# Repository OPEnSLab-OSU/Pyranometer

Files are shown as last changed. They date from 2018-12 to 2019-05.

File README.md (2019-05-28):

# Senior-Project-Group3-Pyranometer
Senior Project featuring the OPEnS Pyranometer radiation sensor.

# What is a pyranometer?
Pyranometers are a tool used to measure solar radiation. A typical pyranometer will gather data on the UV, IR, visible spectrum, and full spectrum solar radiation hitting the surface of the earth at a particular spot. This information could be used to help solar panel research, agricultural research, or climate change research. 

The aim of this project was to make an open-source and low-cost. To do this, this pyranometer takes more time to set up. With low-cost electronics and a 3D printer, this pyranometer can be recreated. Currently, it needs two pieces of hardware - a node and a hub. The node sends the measured data to the hub (up to 5km without building interference) where the hub uploads the data to a Google spreadsheet in live time.

# How to set up
The [Setup_Instructions_For_Grading file](https://github.com/OPEnSLab-OSU/Pyranometer/edit/master/README.md/Setup_Instructions_For_Grading.md) contains step by step instructions on what to gather and how to upload the code for this project. The [Assembly_Instructions file](https://github.com/OPEnSLab-OSU/Pyranometer/edit/master/Assembly_Instructions.md) has more in depth information on necessary materials and 3D printing instructions. In that file, the cost of each material is displayed as well as containing some basic flashing instructions.

# Description of other files and folders on this repo
The [LOOM folder](https://github.com/OPEnSLab-OSU/Pyranometer/edit/master/LOOM) holds the code (using OPEnS lab LOOM 1 architecture) for the pyranometer. The node measures and reports data, while the hub is a receiver for loom and uploads data via PushingBox. The [CAD folder](https://github.com/OPEnSLab-OSU/Pyranometer/edit/master/CAD) contains files to make the 3D design. There are also folders containing documents for the [Fall](https://github.com/OPEnSLab-OSU/Pyranometer/edit/master/Fall2018Docs) and [Spring](https://github.com/OPEnSLab-OSU/Pyranometer/edit/master/Spring2019Docs) terms of the senior capstone class. There is also a file of informal [tips for picking up the project](https://github.com/OPEnSLab-OSU/Pyranometer/edit/master/Tips-on-continuing-the-project).

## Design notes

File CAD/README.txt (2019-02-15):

STL files are completed models that can be sliced and printed. 
F3D files can be opened in Fusion 360 and edited.

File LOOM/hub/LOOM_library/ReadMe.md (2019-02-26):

# Project Loom: Library

This is the primary location of the Project LOOM code, consolidated into place with a single Arduino .ino sketch built with code selected by the preprocessor based on the configuration file. 

## Table of Contents

1. [Installation](#installation)
2. [Device Support](#device-support)
3. [Communication Platforms](#communication-platforms)
4. [Device Configuration](#device-configuration)
5. [Max/MSP](#max/msp)
6. [Library Architecture](#library-architecture)

    1. [Overall Structure](#overall-structure)
        1. [Example Library Include Hierarchy](#example-library-include-hierarchy)
    2. [Adding to the Library](#adding-to-the-library)
    3. [Adding to the Message Router](adding-to-the-message-router)
7. [Channels](#channels)
    1. [Implementation](#implementation)
    2. [Additional Devices](#additional-devices)
8. [Configuration File](#configuration-file)
9. [API](#api)

    1. [Includes](#includes)
    2. [Setup](#setup)
    3. [Main Loop Functions](#main-loop-functions)
        1. [Receive Bundle](#receive-bundle)
        2. [Process Bundle](#process-bundle)
        3. [Measure Sensors](#measure-sensors)
        4. [Package Data](#package-data)
        5. [Send Bundle](#send-bundle)
        6. [Additional Loop Checks](#additional-loop-checks)
        	. [Minimal Working Example](#minimal-working-example)	
10. [SD Card Support](#sd-card-support)
11. [Real-Time Clock Support](#real-time-clock-support)
12. [Arduino IDE Setup](#arduino-ide-setup)
13. [Building and Uploading Code Without The IDE](#building-and-uploading-code-without-the-ide)
14. [Configuration Conflicts](#configuration-conflicts)
15. [Device Identification Hierarchy](#device-identification-hierarchy)
16. [Using the Loom Library](#using-the-loom-library)
17. [Extending Loom Functionality](#extending-loom-functionality)
18. [Example .ino Loop Contents](#example-.ino-loop-contents)      

## Installation

The Loom Library, and any dependencies, need to be placed into the Arduino libraries folder, i.e:

Document > Arduino > Libraries

## Device Support

- Adafruit Feather M0
- Adafruit Feather 32u4

## Communication Platforms

WiFi and LoRa have had the most attention in development and thus have the most support and options, especially WiFi, as that is currently the only to communicate with a computer running Max/MSP. Other platforms have been implemented however. Below is the table of device inputs and outputs currently implemented, planned, or in consideration (bold for well implemented, * if partially implemented or in need of testing to be considered well implemented, plaintext if planned but not implemented, ? if in consideration). The top section is device-device communication platforms, and the bottom section are platforms that do not necessarily transmit directly to another Loom device

| Inputs         | Outputs                     | Comments                                                     |
| -------------- | --------------------------- | ------------------------------------------------------------ |
| **WiFi**       | **WiFi**                    | Implemented                                                  |
| **LoRa**       | **LoRa**                    | Implemented                                                  |
| nRF*           | nRF*                        | May need more testing to be 'proven'                         |
| Ethernet       | Ethernet*                   | Currently only used with hubs, expansion in progress         |
| GSM            | GSM*                        | Currently only one device, so outputs MQTT via GSM, but no GSM receiving yet |
| Bluetooth      | Bluetooth                   | Planned                                                      |
|                |                             |                                                              |
| Google Sheets? | Google Sheets (PushingBox)* | Works as output, looking for ways of improving the pipline   |
| Adafruit IO*   | Adafruit IO*                | Could use more robust integration                            |
| IFTTT?         | IFTTT?                      | Currently, IFTTT works only as output though Adafruit IO     |
| SD card?       | **SD card**                 | Works as output, considering as input                        |
| Serial?        | **Serial**                  | Works for output. Serial as input may or may not be useful (is how Fona is tested) |

## Device Configuration

The configuration of the code to upload and flash to devices is set in the config.h file. This file presents the options that can be set or toggled to achieve a particular behavior. The preprocessor uses these definitions to select the necessary declarations, variables, and functions automatically. 

Currently changes to the config need to be done manually in the file itself. A script to automate this process from the command line, and ultimately Max, is in progress.

## Max/MSP

The associated [Loom Data Processors](https://github.com/OPEnSLab-OSU/InternetOfAg/tree/master/Max) and control modules are made as patches in Max/MSP. The Max interfaces are not strictly necessary for using this library, but provide convenient features and means of interacting with your Loom devices / network.

## Librarary Architecture

The LOOM Library is the answer to the growing set of code to drive Project LOOM's supported devices, hardware, and communication platforms. The set of possible combinations of device configurations makes it unfeasable for LOOM developers and users alike to manage sketches with desired functionality. Instead, a configuration file effectively creates the desired sketch dynamically. A loom_preamble file selects entire files to include, each of which may also contain additional preprocessor statements.

### Overall Structure

The LOOM Library is effectively an aggregate of all of the functionality possible within the entirety of the supported devices, sensors, and actuators. The user then specifies the needs of their sketch inside the config.h. Based on the needs of the sketch, the requisite files, functions, and logic will be dynamically included such that only what is needed by the sketch is uploaded to the device. loom_preamble.h uses config.h to know which files to include, these files in turn then include the libraries they need. loom_common.h is also always present as it has the LOOM_begin() function, which sets up all the modules and sensors being used by the sketch. 

#### Example Library Include Hierarchy

The hierarchy of included files looks something like the following (example if building for Ishield device on Feather M0 WiFi). 

**Note** – bolded are files that are always necessary and thus included, independent of config.h. In angle brackets are non-Loom dependencies.

- Ishield_Example.ino
  - **Config.h**
  - **Loom_preamble.h** (likely to be renamed)
    - **<OSCBundle.h>**
    - Loom_translator.h
    - <Adafruit_SleepyDog.h>
    - <SPI.h>
    - loom_analog.h
    - loom_neopixel.h
      - <Adafruit_NeoPixel.h>
    - loom_mpu6050.h
      - <I2Cdev.h>
      - <Wire.h>
      - <MPU6050_6Axis_MotionApps20.h>
    - loom_wifi.h
      - <WiFi101.h>
      - <WiFiUDP.h>
    - **loom_flash.h**
      - <FlashStorage.h>
    - **loom_common.h**

### Adding to the Library

New sensor and actuator support can be added by filling out the loom_mod_template.h file with relevant code. This template ensures that the code for each piece of hardware conforms to a standard format, making it easier to read and understand.

New files should be added #included in the loom_preamble.h file after config.h but generally before loom_flash.h and loom_common.h.

There are plans/consideration for a script that will handle most of the additions for a user based on various provided parameters / needs as current additions generally need to modify the config, preamble, loom_commom (sometimes), and loom_interface files in a mostly boiler plate fashion in addition to the new device-specific file.

### Message Router

#### Intro to Route and Dispatch of Message Router

Custom functions can be added to the message router. The message router is called via:

```
bndl->route(configuration.packet_header_string, msg_router);
```

From the `process_bundle` function in the 'loom_interface.h' file. The message router checks any OSC messages that it receives, and if the message's address string matches one of the dispatch calls in the router, then the message gets forwarded to a function designed to handle / process messages with that address string. This usually entails reading the arguments to the message (which should be sent in an order / format known by the function that will handle the processing).

The dispatch calls in the message router take the following form:

```
msg.dispatch("/address", processing_function, addrOffset);
```

An example of a dispatch that takes a message that has an address of the device identifying string followed by "setID", and calls a function `set_instance_num` (which sets the device instance number) would be:

```
msg.dispatch("/SetID", set_instance_num, addrOffset);
```

The reason only the `/SetID` is provided and not something like `/LOOM/Ishield7/SetID` is because the aforementioned route function checks for message addressed to the device, which in this case is identified by `/LOOM/Ishield7`, and passes only the remaining part of the address to the message router. Messages that do not start with the device indentifying string are not sent to the message router.

#### Adding Custom Functions to Message Router

There are a few steps that must be followed in order to get a custom function to be callable by the message router. These are:

- Write your function in the correct format
- Add the function prototype to the top of loom_msg_router.h file
- Add the dispatch call to the msg_router function

**Writing Your Function**

All function that are called by the message router need to take only an OSC message by reference, and return nothing. Thus a function skeleton would look like:

```
void your_function(OSCMessage &msg)
{
	// process the message forwarded from msg_router
}
```

Inside this function is generally where you will process the message (if you need, you can add auxiliary function(s), to do some of the processing/handling - these do not have constraints on the parameters or return value). The following OSC methods are recommended for extracting the arguments from the message. (The below list is not exhaustive, see the [OSC API](https://github.com/CNMAT/OSC/blob/master/API.md) for more functions)

**`msg.size()`** Returns the number of arguments in the the message

**`msg.getType(index)`** Returns the type of the argument at `index`, `i` for integer, `f` for float, and `s` for string. Useful in combination with switch statement to select which of the following three functions to call.

**`msg.getInt(index)`** Returns argument to message that is an integer at `index` if argument is indeed an integer and there is an argument at that index

**`msg.getFloat(index)`**Returns argument to message that is a float at `index` if argument is indeed a float and there is an argument at that index

**`msg.getString(index)`**Returns argument to message that is a string at `index` if argument is indeed a string and there is an argument at that index

**`msg.getAddress(buf, 0);`** Copies address of message into char array called `buf`

**Adding the Function Prototype**

Add the protype of the function you wrote, e.g:

```
void your_function(OSCMessage &msg);
```

to the `Custom Function Prototypes` section at the top of the `loom_msg_router.h` file. (Don't forget the semicolon). Should be no need to add the prototypes for any auxililary functions called by the `your_function`.

**Adding the Dispatch Call**

At the bottom of the message router, add:

```
msg.dispatch("/command/string", your_function, addrOffset);
```

Where

-  `/commmand/string` is the section after the device identifying string that is being used to select which function to dispatch a message to. This should be descriptive but not overly long. In the above example,  the string `setID` was used to check if the message should be forwarded to `set_instance_num`
- `your_function` is the name of the function you want to be called if the message matches the device identifying string and command string.
- `addrOffset` should stay as it is, this is an integer value passed in from the `bndl->route(...)` call, and simply specifies where in the message string to start looking for the command section (i.e. right after the device identifying string)

## Channels

The LOOM library and associated Max/MSP processors are designed to use channel based interfaces by default. Channel interfaces abstract device instance number, UDP port, and IP address into a single letter A, B, C, … H. 

The channels are purely a convenience, and the devices can operate without any notion of channels in the firmware and/or Max patches.

### Implementation
A common port is used for the communication of device settings in order to allow the Max patches to communicate with devices in a consistent manner if the instance number, UDP port, or IP (i.e. the channel information) address are unknown.

**Common Port:** 9440 

**Device Unique Channnel Data:** 9441 – 9448

Channel A:	Instance # = 1		UDP Port = 9441	

Channel B:	Instance # = 2		UDP Port = 9442

• • •

Channel H:	Instance # = 8		UDP Port = 9448

**IP Address:** Automatically assigned to devices by one's router. Max interfaces will automatically fetch IP address of selected device. If not using the channels feature implemented in the Loom Max interfaces, then Loom Debug mode may need to be enabled, or the user may need to add custom code, in order to obtain the device's IP address.

### Additional Devices

The Max interfaces presently support 8 concurrent channels, the library itself poses no such restrictions and using custom Max interfaces can allow for the control of more devices.

## Configuration File

The configuration file is used in conjunction with preprocessor statements to essentially built the specified sketch. Any options that can be set or toggled, or any specification of hardware (e.g. sensors and actuators) being used occur in (and only in) this config.h.

Any options for custom additions to the library should be added only to the configuration file.

The config.h file needs to be included before the library itself, so that the configuration can be used to define the necessary subset of the library.

## API

### Includes

Only the configuration and the library are necessary in the .ino sketch. All necessary dependecies of the Loom Library are automatically included. 

**Note:** The config.h file must precede the library

```cpp
#include "config.h"
#include "loom_preamble.h"
```

### Setup

All Loom and device setup is called dynamically within Loom_begin(). A simple setup function would simply be:

```cpp
void setup() 
{
	Loom_begin();	
    
    // Any custom setup code
}
```

### Main Loop Functions

The Loom Library has six primary interface function to call. With just these, a fully functional sketch can be made. Custom code can be inserted before, between, and after any of the interface functions, but changing the relative ordering of the interface functions is not recommended unless you know what you are doing.

#### Receive Bundle

Fills an OSC bundle with packets received the specified platform if data exists and platform is enabled.

```cpp
// Receive bundles
//  takes bundle to be filled and wireless platforms [WIFI, LORA, NRF]
receive_bundle(&bndl, WIFI);
```

- **bndl** – The bundle to fill
- **platform** – The wireless platform to receive on, the values are encoded to a Platform enum to reduce chance for errors

#### Process Bundle

Examine the provided OSC bundle (presumably filled via receive_bundle(). If bundle is not empty,  has no errors, and is addressed to this device, then attempt to perform action specified.

```cpp
// Process bundle (nothing will happen if bndl is empty), bundle is emptied after processing
process_bundle(&bndl);
```

- **bndl** – The bundle to be processed

#### Measure Sensors

Update stored readings from sensors by calling measure on each enabled sensor.

```cpp
// Update stored readings from sensors
measure_sensors();
```

#### Package Data

Fill the provided OSC bundle with latest stored sensor readings

```cpp
// Populate bundle to send with sensor values
package_data(&send_bndl);
```

- **send_bndl** – The OSC bundle to be filled

#### Send Bundle

Sends a packaged bundle on the specified platform

```cpp
// Send the bundle
//  takes bundle to be filled and wireless platforms [WIFI, LORA, NRF]
send_bundle(&send_bndl, WIFI);
```

- **bndl** – The bundle to be sent
- **platform** – The wireless platform to send on, the values are encoded to a Platform enum to reduce chance for errors

#### Additional Loop Checks

Performs any miscellaneous Loom tasks that happen each loop iteration, but are not handled by any of the other 5 interface functions, such as delays between loop iterations and checking a device button has been held for a set amount of time.

```cpp
// Loop checks and sleep between iterations if enabled
additional_loop_checks();
```

### Minimal Working Example

This example is fully functional. It assumes that WiFi has been specified as a wireless communication platform in the config.h file.

```cpp
#include "config.h"
#include "loom_preamble.h"

void setup() 
{
	Loom_begin(); // LOOM_begin calls any relevant LOOM device setup functions
	// Any custom setup code
}

void loop() 
{
	OSCBundle bndl, send_bndl; 
	
	receive_bundle(&bndl, WIFI);
	process_bundle(&bndl);
	measure_sensors();
	package_data(&send_bndl);
	send_bundle(&send_bndl, WIFI);
	additional_loop_checks();
} 
```

## SD Card Support

The Loom library extends the Arduino SD library to have more features, mostly tailored towards using common data structures used by the library.

Namely, support for printing:

- Single elements (int, floats, c-strings, Strings)
- Arrays (ints, floats, c-strings, Strings)
- Bundles (single or multi-msg format)

Additionally, if used with MaxMSP, there is support for sending commands to enable / disable the logging of bundles the device receives (also works without Max).

## Real-Time Clock Support

The Loom library supports two RTC devices:

- Adafruit DS3231 
- Adafruit PCF8523

Currently, interrupts are only supported via the DS3231, with the PCF8523 mostly being used in conjunction with an SD card (as Adafruit Adalogger featherwing has PCF8523 and SD card holder) to provide timestamps.

The Loom Library has support for both devices for returning strings of the date, time, or weekday. Additional timer functions are provided for the DS3231.

## Arduino IDE Setup

Make sure to download the dependencies of the Loom Library from:

https://github.com/OPEnSLab-OSU/InternetOfAg/tree/master/Dependencies 

and install the libraries with the Arduino IDE, as described here:

https://www.arduino.cc/en/guide/libraries

## Building and Uploading Code Without The IDE

Work is currently be done on investigating and implementing a script that will build the config.h file from the command line, taking the options as arguments. A corresponding Max interface will be made to provide a GUI to these options. The interface will pair with the one to subsequently build and upload code to devices.

The design is planned to be as follows:

- Generate the config file from command line 
  - Arguments to used set options, have default values if none specified
  - Sent to a Python script, inserting the parameters in the relevant locations of the config file
- Be able to call this script from Max
- Use Max to create a graphical interface of toggles / inputs corresponding to the script arguments.
  - Error checking (i.e., of selection conflicts) can be performed in the script or Max, but would doing so in Max would give users immediate feedback on invalid combinations

## Configuration Conflicts

The following combinations of options in the configuration file result in various conflicts (e.g. of dependencies) that are known to result in errors or undefined behavior. Such conflicts are also mentioned in the config.h file itself.

- LoRa + nRF
- is_sleep_period + LoRa (Adafruit_ASFcore-master/tc_interrupt.c:140: multiple definition of 'TC3_Handler')

## Device Identification Hierarchy

In Loom, a device is uniquely identified by 4 elements, from broad to precise identification:

- Family
- Family number
- Device type
- Device number

The OSC messages and bundles send to and from devices are address/signed with their ID string, in the following format:

`/<Family><Family-Num>/<Device-Type><Device-Num>/<the-rest-of-the-address>`

For example, Ishield 7 in the 3 'Loom' subnet would be:

`/Loom3/Ishield7`

**Family**

A family is generally a complete network of a given functionality under a single person or group.

**Family Number**

A family number is used to distinguish subnets between a family. This is typically used to seperate devices into groups by purpose, location, etc. In Max/MSP, you will generally only be observing a single subnet at a time. Family numbers should be 0 or greater.

**Device Type**

The Loom Library supports an autoname feature to try to name your device if it fits into a common hardware / functionality set. These include devices like Ishields, multiplexers, servo controllers, etc. and name the device accordingly. Alternatively, you can use custom names for your devices if you want. 

**Device Number / Channel**

A device number is used to distinguish the devices on the same subnet (family number) that have the same device type. Device numbers are sometimes also referred to as channels. Device numbers are expected to be between 1 and 8, inclusive (channels A-H).

### WiFi UDP Ports

If using WiFi, the family number and device number will determine the UDP ports that the device will expect messages from. The device will check and send on 3 ports, one for global messages, one for subnet, and one for device specific messages. The calculation of the specific ports are shown below. The reason for different ports fro various devices/purposes is to reduce the number of messages a device may recieve that were not intended for it.

### Device Targetting Scope

The message routing function of the Loom Library supports receiving messages addressed at a global, subnet, or device level. Max/MSP can send on any of the 3 formats as well.

**Global** 

Broadcast the OSC bundle to all devices. Those with the matching family name can see/react to the message. If using WiFi the message is sent on UDP port `9400`.

`/<Family>/<command>`

**Subnet**

Broadcast to a single subnet of a given family. Those with the matching family name and family number can see/react to the message. If using WiFi the message is sent on UDP port `9400+10*(family-num)`.

`/<Family><Family-Num>/<command>`

**Device**

Target a message at a single device, i.e. the one with the matching family, family number, device type, and device number. If using WiFi the message is sent on UDP port `9400+10*(family-num)+(device-num)`.

`/<Family><Family-Num>/<Device-Type><Device-Num>/<command`

### Diagram of Device Scope

Loom_Hierarchy_Diagram

## Using the Loom Library

This section assumes that you want to use the Loom Library without integrating your code, software, or hardware formally into the library's official code. This means that your code and modifications will exist almost exclusively in the main .ino file and config.h file.

**Config.h**

The configuration file is where you will define which Loom supported components are being used, and various associated options and behaviors. Any functionality you need beyond Loom will be defined in the .ino file or your own addition files to #include.

 **.ino Sketch**

By default, the .ino sketch is fairly sparse – the config.h and Loom preamble are #included (which together define what parts of the library should be used). The `setup()` function simply calls `Loom_begin()`  to handle any of the setup of the Loom components. The `loop()` function declares an OSC Bundle or two and uses the [API functions](#api). 

- Any global variables you need that are not already availalbe in Loom can be added above the `setup()` function
- Add any additional setup you need after the call to `Loom_begin()` in `setup()`
- Use the API to interface with the supported components of Loom at a high level
- Put your own code into the `loop()` function as needed to support your additional functionality / components

## Extending Loom Functionality 

This section will describe some of the ways that you can extend Loom without officially integrating code into the library. 

**Adding Message Router Options**

If you have a non-Loom actuator that you would like to be able to respond to OSC Bundles, refer to the `loom_mod_template_actuator.h` for how to setup a function to handle messages forwarded from the message router, which directs messages to the correct 'driver' function for processing. 

Then you need to add routing to your function in the message router (in `loom_msg_router.h`. Follow the format of the other dispatches in the function, i.e:

```
if (msg.dispatch("/<some-command>", <function-to-call>, addrOffset) ) return;
```

## Example .ino Loop Contents

This section provides some common examples of how you might format the `loop()` function in the .ino file.

#### WiFi Send and Receive

```
void loop() 
{
	OSCBundle bndl, send_bndl;  		// Bundles to hold incoming and outgoing data

	receive_bundle(&bndl, WIFI);		// Receive messages
	if (bndl.size()) {
		print_bundle(&bndl);			// Print bundle if LOOM_DEBUG enabled
	}
	process_bundle(&bndl);				// Dispatch message to correct handling functions

	measure_sensors();					// Read sensors, store data in sensor structs
	
	package_data(&send_bndl);			// Copy sensor data from state to provided bundle
	
	send_bundle(&send_bndl, WIFI);		// Send bundle of packaged data

	additional_loop_checks();			// Miscellaneous checks
}
```

#### LoRa Hub (Recieve from node, upload to Google Sheet, no sensors)

```
void loop() 
{
	OSCBundle bndl;  					// Bundles to hold incoming and outgoing data

	receive_bundle(&bndl, LORA);		// Receive messages
	
	log_bundle(&bndl, PUSHINGBOX);		// Send bundle of packaged data

	additional_loop_checks();			// Miscellaneous checks
}
```

#### LoRa Sensor Node (Transmits to central hub for upload to Google Sheet)

```
void loop() 
{
	OSCBundle send_bndl;  				// Bundles to hold incoming and outgoing data

	measure_sensors();					// Read sensors, store data in sensor structs
	
	package_data(&send_bndl);			// Copy sensor data from state to provided bundle
	
	send_bundle(&send_bndl, LORA);		// Send bundle of packaged data

	additional_loop_checks();			// Miscellaneous checks
}
```

#### 

####

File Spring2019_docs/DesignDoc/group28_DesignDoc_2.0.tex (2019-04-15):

\documentclass[10pt,draftclsnofoot,onecolumn,letterpaper]{article}
\usepackage{ragged2e}
\usepackage[svgnames,table]{xcolor}
\usepackage[hidelinks]{hyperref}
\usepackage{enumitem}

%\usepackage{pgfgantt}
\usepackage{graphicx}
    
\usepackage[utf8]{inputenc}
\usepackage[left=0.75in, right=0.75in, top=0.75in]{geometry}
    
\usepackage[T1]{fontenc}
\setlength{\parindent}{0pt}
\newlist{tabitem}{itemize}{1}
\setlist[tabitem]{wide=0pt, nosep, leftmargin= * ,label=\textbullet,after=\vspace{-\baselineskip},before=\vspace{-0.6\baselineskip}}

\begin{document}
\begin{Center}
{\fontsize{14pt}{16.8pt}\selectfont OPEnS Pyranometer: IoT Solar Radiation Sensor\\ Project Requirements\par}
\end{Center}\par
    
\begin{Center}
Garen Porter, Brooke Weir, Alejandro Tovar\\
\end{Center}\par
\hrule
\begin{Center}
{\fontsize{12pt}{16.8pt}\selectfont \textbf{Abstract}\par}
\end{Center}\par
    
{\fontsize{10pt}{12.0pt}\selectfont The IoT solar radiation sensor, referred to as the pyranometer, is to be a wireless and open-source solar radiation sensor that integrates into the OPEnS Lab IoT architecture. The goal of this project is to create a completely open-source pyranometer that is comparable to commercial-grade pyranometers that can cost thousands of dollars. The pyranometer will be able to sense and record some combination of UV, IR, and visible spectrum solar radiation hitting the pyranometer and transmit the data to a remote data hub. The pyranometer will record accurate data, last weeks in the field on battery power, and be able to survive most climates.
\par}\par
    
\newpage

\tableofcontents

\newpage

% 8. now you write!
\section{Revisions}

\setlength{\arrayrulewidth}{1mm}
\setlength{\tabcolsep}{20pt}
\renewcommand{\arraystretch}{2}
{
\begin{table}[h]
\begin{tabular}{ |p{4cm}|p{3cm}|p{7cm}|  }
\hline
Section & Original & New \\
\hline
Functional Requirements
& 
Using two sensors to gather data
& 
Using three sensors to gather data \\
\hline
Physical Characteristics
&
Teflon is a needed material
&
\begin{tabitem}
    \item TCA9548A is as a needed material 
    \item SI1145 is a needed material 
    \item Adalogger Featherwing is a needed material
    \item 3.7v Lipo battery is a needed material
    \item Acrylic domes are a needed material
    \item Teflon is not a needed material
\end{tabitem}
\tabularnewline
\hline
\end{tabular}
\end{table}
}

\newpage

\section{Introduction}
\subsection{System Purpose}
Pyranometers already exist, but they are expensive and do not integrate into the Loom architecture being used in the OPEnS lab. More specifically, open-source pyranometers exist, but they are typically poorly documented, not wireless, and not validated against comercial-grade pyranometers. Researchers need an open-source pyranometer that can be made inexpensively, wirelessly communicate with the Loom system, and be able to withstand a wide range of climates. As of now, the only way to acquire a wireless pyranomter is to buy it, and this project looks to eliminate that requirement by allowing scientists to assemble their own pyranometer using open-source CAD files, open-source software, and a microcontroller. Scientists will be able to assemble the pyranometer, place it in the field, and watch data be gathered in real time from any device with internet connectivity; all of this at an affordable price.  

\subsection{System Scope}
The system to be produced is titled "OPEnS Pyranometer: IoT Solar Radiation Sensor".\\\\This system will detect a combination of UV, IR, and visible spectrum solar radiation. The solar radiation will be translated into $W/m^2$ and then uploaded to a Google Spreadsheet in real time. The data acquired will be accurate, with an $R^2$ value greater than 0.8. The system will be able to withstand high temperatures, be weatherproof, and be able to remain in the field for weeks at a time. The software and files required to build the system will be free and open-source, and documentation will be available to help users build the system. The system will be easy to integrate into the Loom architecture, and the system will notify users when the pyranometer has gone offline or otherwise stopped communicating with the data hub. The system will not be solar powered, and batteries will need to be recharged periodically.\\\\At the highest level, scientists will be able to gather real-time solar radiation data from a remote device. The pyranometer can be left in the field for weeks at a time, and scientists will be able to continually see the data being acquired. This will help scientists study how solar radiation effects the environment as well as how it effects climate change. Scientists will be able to download open-source CAD files to 3D print the housing structure for the pyranometer. The software will also be able to be freely downloaded and flashed onto a microcontroller. Documentation will exist to guide users to assemble the pyranometer and synchronize it with the Loom system. Users will then be able to deploy the system and immediately begin using it. The pyranometer will be easy to assemble and deploy. The data gathered from the system will be accurate with an $R^2$ value greater than 0.8. The system will be able to withstand high temperatures and be otherwise weatherproof. In the case that the system does go down, users will be notified immediately. The system will be able to last weeks at time, with batteries being periodically recharged.

\subsection{System Overview}
\subsubsection{System Context}
The pyranometer requires users to set up the sysetm in an area where they wish to acquire data. The pyranometer will then take solar radiation and convert it into $W/m^2$ and transmit it to a data hub. From there, the data hub will upload the data to a Google spreadsheet where users will be able to interpret and use the data.

\subsubsection{System Functions}
Per our client's request, we are exploring three different designs. In one design, the pyranometer will be able to take in solar radiation and convert it into heat using a black body object. Then a thermal sensor will read the change in heat and pass the data to a processing chip. From there a microcontroller will translate the data into $W/m^2$. The raw analog data is useless to researchers, so the translation into $W/m^2$ is necessary for usability. Our second design will be using a photo diode to take in light directly. A light diffuser will be used to evenly spread out the light onto the diode. The diode will output analog data that will need to converted to digital data. Again, we will have to use a microcontroller to translate the data into $W/m^2$. The final design will use a lux sensor. The lux sensor is similar to the photo diode, but it reads UV, IR, and full spectrum radiation separately. The solar radiation data will be translated to $W/m^2$. Each pyranometer design will be able to read a combination of IR, UV, and visible spectrum. The data will be transmitted wirelessly and in real time to a data hub. The entire system will also be integrated into the Loom IoT architecture.

\subsubsection{User Characteristics}
The user will be able to configure our sensor using the open source software provided and calibrate it to their specifications. When turned on, the pyranometer will instantly process data from any source of solar radiation and transmit it to a data sheet in real time. The user should be able to use deploy the pyranometer to all kinds of environments and still gain accurate and consistent data. The user will be notified when the pyranometer goes into an offline state and it should not be difficult to fix the pyranometer or replace parts.

\subsection{Definitions} Loom: Software architecture surrounding OPEnS sensors\\$W/m^2$: Watts per meters squared; the standard unit of measurement for solar radiation\\Weatherproof: Capable of withstanding rain, high temperatures, low temperatures, wind, and be waterproof.

\section{System Requirements}

\subsection{Functional Requirements}
There is no material that lets UV, IR, and visible spectrum solar radiation through; meaning that at least one form of solar radiation will not make it through the dome and reach the sensor. Multiple materials will be needed to get readings from the three types of solar radiation. Three sensors will be needed, one behind acrylic and the other two behind glass. One sensors will detect UV radiation, one sensor will detect visible spectrum radiation, and the third sensor will detect IR. Our processing chip needs to be able to read data from all three sensors and accurately combine the data to report the total $W/m^2$ hitting the black-body object. The structure surrounding the sensors, microcontroller, and batteries needs to be weatherproof in order to withstand various climates. The radio that sends data to the data hub needs to reach at least ten kilometers in various climates, and the antennae needs to be weatherproof. The batteries should be able to last a few weeks and be easy to recharge. The optical black object that traps heat needs to be black enough to accurately report the amount of solar radiation hitting it. Finally, data needs to be translated from analog voltage to energy ($W/m^2$).

\subsection{Usability Requirements}The effectiveness of the Pyranometer will be measured by the accuracy of the data it produces, its survivability in the field, its ability to transmit data wirelessly, and its ability to stay on for long periods of time. To test the data accuracy, we will compare the data of our pyranometer with the data of a commercial-grade pyronometer. To test surviveabilty, different climates will be simulated using greenhouses and sprinklers. Testing how long the pyronometer will last is as simple as leaving it active and timeing how long it takes for it to die. We can test the range of the radio by moving the pyranometer further and further away from the data hub and noting the limit of the radio's range.

\subsection{Performance Requirements}The pyronometer, once built, should be "plug and play". Once it is deployed and turned on, it should sense varying levels of solar radiation and be able to accurately report changes in solar radiation over time (changes in overall solar radiation and changes in specific types of solar radiation). The pyronemeter is expected to be weatherproof, and thus go undamaged when deployed to the field. While deployed, the pyranometer's power supply should last a minimum of three weeks. It is expected that the pyronometer is uploading data non-stop while deployed, no matter the time of day or weather conditions.

\subsection{System Interface}
The interface for the pyranometer will include an intuitive way for users to power on the device. The online interface will be a Google Spreadsheet that updates periodically with data from the pyranometer.

\subsection{System Operation}
The pyranometer will be well documented and users will be provided with thorough, easy to follow instruction on how to assemble and deploy the pyranometer. The pyranometer should be "plug and play", in that it will work properly once it is deployed and turned on. One of the main goals for the pyranometer project is to have it be easy to assemble, so a simple design and thorough instructions will make the pyranometer easy to build and use.

\subsection{System Security}
Keeping OPEnS lab projects secure is a top priority, so chips that do not support full operating systems will be used to control and operate the pyranometer. The microcontroller that operates the pyranometer will not support SSH (secure shell) and should be difficult to hack. The data reported by the pyranometer will be uploaded to Google sheets via a PushingBox API that translates the data into HTTPS.

\subsection{Physical Characteristics}
The only constraint on weight, volume, and dimension is that it is able to carried by one person. The system is meant to be built and configured inside a lab with access to a 3D printer. The pyranometer is meant to be deployed in an outdoor location that is in range of a Loom data hub. The materials used are custom PCB, an Adafruit TSL2591, a Thermopile TMP007, an Adafruit SI1145, an Adafruit TCA9548A, an Adalogger Featherwing, an Adafruit Feather-M0, a 3.7v Lipo battery, an antennae, ABS plastic, acrylic, and glass. The parts are not interchangeable, as the software is written for specific hardware and the materials block specific solar radiations. The enclosure and domes are to be 3D printed, and the glass and acrylic should not have to be shaped in any way.

\subsection{Environmental Conditions}
The pyranometer will be deployed outdoors, so it will be subject to all natural environmental conditions. This includes wind, rain, and various temperatures. Wind has the potential to blow the antennae off, low temperatures can skew thermopile data, and high temperatures can cause overheating. Measures must be taken to prevent all of these from happening, as any of them can ruin the effectiveness of the pyranometer. The pyranometer utilizes several electronic parts, so any water leaking into the pyranometer will cause significant damage; thus the pyranometer will be made waterproof and the hardware will be coated with a waterproof substance.

\subsection{Information Management}
The optical black within the material absorbs solar radiation in the form of heat. A thermopile reads the change in heat of the optical black and outputs analog voltage. The microcontroller translates the analog voltage into $W/m^2$ and sends the data to a data hub over radio. The data hub expects $W/m^2$ data. Additionally, the other two sensors record UV, IR, and visible spectrum data and send it to the microcontroller. The mincrontroller translate the raw data into $W/m^2$ and sends it to the data hub.

\subsection{System Lifecycle Sustainment}
To realize a quality system, the pyranometer will have to be tested. The best tool to review the system is an industry-grade pyranometer that our open-source pyranometer will be compared to. We will compare the data from the two pyranometers to be able to determine how accurate our pyranometer's data is. We will use a greenhouse and sprinklers to simulate various weather conditions. Before integrating the system into Loom, the data from the pyranometer will be uploaded to an SD card and analyzed. Having everything be open-source, people will be able to continually improve the software and design.

\section{Verification}
There are four areas to verify: quality of data, survivability, data transmission, and portability. To test quality of data, we will take a commercial-grade pyranometer and gather data samples. That data will be compared against the data taken with our pyranometer to determine the accuracy of the data. Each pyranometer will be used in the same controlled environments to help ensure accuracy.\\\\ Survivability involves the pyronometer being weatherproof and being able to last at least 3 weeks in the field. To verify how long the pyranometer can remain actively deployed, we will work with the OPEnS staff to perform a draw test and estimate the longevity of the pyranometer. The estimated time of life must be at least 21 days. To verify surviveability, we will simulate different environments. To simulate a hot and humid environment, we will place the pyranometer in a greehhouse, and to simulate rain we will place the pyranometer in the midst of a sprinkler system.\\\\To verify data transmission, the pyranometer will wirelessly transmit data at gradually increasing distances (intervals of one kilometer). This will verify that wireless data transmission is functional, and it will give an upper bound to the range of the wireless transmission. This will verify the range is long enough (at least ten kilometers).\\\\Portability refers to ease of use and deployment. To verify this, we will give a user an assembled pyranometer and deployment documentation. We will observe how they are able to follow the documentation and if they are able to successfully deploy the pyranometer and get data readings.

\section{Appendinces}
\subsection{Assumptions and Dependencies}
It is assumed that the pyranometer will be used to integrate with Loom, as such the radio will be programmed to communicate with a Loom data hub.

\subsection{Acronyms and Abbreviations}
OPEnS: Openly Published Environmental Sensing; the lab that is developing the pyranometer\\CAD: Computer-aided design; design files used in 3D printing\\IoT: Internet of Things; wirelessly interconnected systems

\pagebreak

\section{Gantt Chart}

\begin{figure}[h]
    \centering
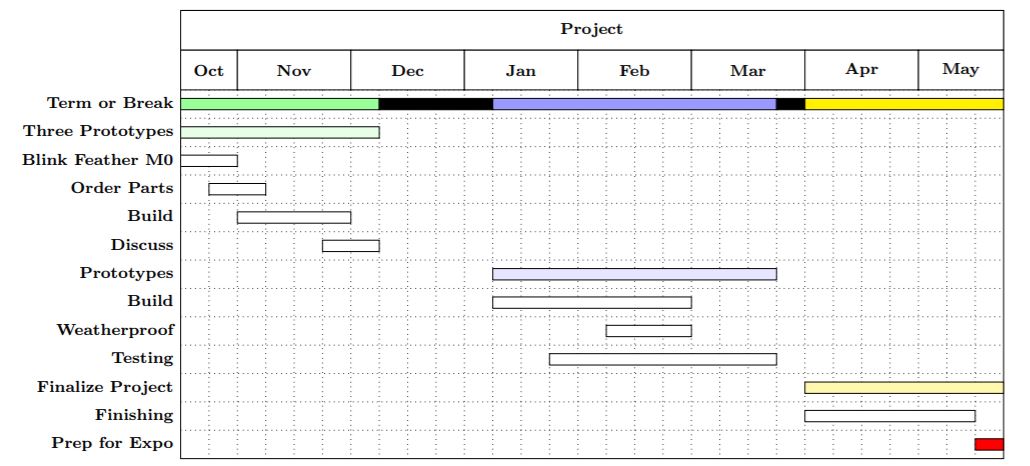
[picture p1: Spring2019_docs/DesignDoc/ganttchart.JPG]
    
\end{figure}

\end{document}

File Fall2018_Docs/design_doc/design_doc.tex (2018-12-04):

\documentclass[10pt,draftclsnofoot,onecolumn,letterpaper]{article}
\usepackage{graphicx}
\usepackage{url}
\usepackage{setspace}

\usepackage{geometry}
\geometry{textheight=9.5in, textwidth=7in}
%\graphicspath{{./images/}}
% 1. Fill in these details
\def \CapstoneTeamName{		Pyranosaurs}
\def \CapstoneTeamNumber{		28}
\def \GroupMemberOne{			Garen Porter}
\def \GroupMemberTwo{			Brooke Weir}
\def \GroupMemberThree{			Alejandro Tovar}
\def \CapstoneProjectName{		OPEnS Pyranometer: IoT Solar Radiation Sensor}
\def \CapstoneSponsorCompany{	Openly Published Environmental Sensing}
\def \CapstoneSponsorPerson{		Chet Udell}

% 2. Uncomment the appropriate line below so that the document type works
\def \DocType{		%Problem Statement
				%Requirements Document
				Design Document
				%Design Document
				%Progress Report
				}
			
\newcommand{\NameSigPair}[1]{\par
\makebox[2.75in][r]{#1} \hfil 	\makebox[3.25in]{\makebox[2.25in]{\hrulefill} \hfill		\makebox[.75in]{\hrulefill}}
\par\vspace{-12pt} \textit{\tiny\noindent
\makebox[2.75in]{} \hfil		\makebox[3.25in]{\makebox[2.25in][r]{Signature} \hfill	\makebox[.75in][r]{Date}}}}
% 3. If the document is not to be signed, uncomment the RENEWcommand below
\renewcommand{\NameSigPair}[1]{#1}

%%%%%%%%%%%%%%%%%%%%%%%%%%%%%%%%%%%%%%%
\begin{document}
\begin{titlepage}
    \pagenumbering{gobble}
    \begin{singlespace}
    	%\includegraphics[height=4cm]{coe_v_spot1}
        \hfill 
        % 4. If you have a logo, use this includegraphics command to put it on the coversheet.
        %\includegraphics[height=4cm]{CompanyLogo}   
        \par\vspace{.2in}
        \centering
        \scshape{
            \huge CS Capstone \DocType \par
            {\large November 27, 2018}\par
            \vspace{.5in}
            \textbf{\Huge\CapstoneProjectName}\par
            \vfill
            {\large Prepared for}\par
            \Huge \CapstoneSponsorCompany\par
            \vspace{5pt}
            {\Large\NameSigPair{\CapstoneSponsorPerson}\par}
            {\large Prepared by }\par
            Group\CapstoneTeamNumber\par
            % 5. comment out the line below this one if you do not wish to name your team
            \CapstoneTeamName\par 
            \vspace{5pt}
            {\Large
                \NameSigPair{\GroupMemberOne}\par
                \NameSigPair{\GroupMemberTwo}\par
                \NameSigPair{\GroupMemberThree}\par
            }
            \vspace{20pt}
        }
        \begin{abstract}
        The wireless, open-source pyranometer project has more to do with hardware than software, thus the design views discussed deal with hardware and physical materials. The project is being sponsored by the OPEnS lab at Oregon State University and there are two stakeholders, Dr. Chad Higgins and Dr. Chet Udell. The pyranometer is to become a part of the environmental sensing collection in the OPEnS lab; it is therefor critical that the pyranometer be able to withstand multiple environments. Most of the physical elements in the pyranometer will relate to weatherproofing or heat regulation in some way and both are crucial in keeping the pyranomator running and reporting accurate data. The pyranometer uses a thermopile to report solar irradiance, so any extra solar energy entering the pyranometer will skew the data. If the data reported by the pyranometer is inaccurate, the pyranometer is rendered useless, thus ensuring accurate data is important part of the design. Each design decision in no way hinders data accuracy, and anything possible is done to potentially increase data accuracy.

        \end{abstract}     
    \end{singlespace}
\end{titlepage}
\newpage
\pagenumbering{arabic}
\tableofcontents
% 7. uncomment this (if applicable). Consider adding a page break.
%\listoffigures
%\listoftables
\clearpage

% 8. now you write!
\section{Introduction}
\subsection{Project Description}
The overall project is a wireless, open-source pyranometer. A pyranometer is a device that detects solar radiation and reports a $W/m^2$ value based on the total amount of solar radiation hitting the device. Open-source pyranometers exist, but they are generally poorly documented and wired. This pyranometer will be easy to set up due to good documentation and will be wireless.
\subsection{Stakeholders}
\subsubsection{Dr. Chet Udell}
Our primary client, Dr. Chet Udell, is the director of the Openly Published Environmental Sensing (OPEnS) lab. The OPEnS lab is the primary sponsor of our project and our pyranometer will become one of the many OPEnS lab wireless sensors.

\subsubsection{Dr. Chad Higgins}
Dr. Chad Higgins is an associate professor in the College of Agricultural Sciences, specically in College of Biological and Ecological Engineering. Dr. Higgins conducts many ecological studies and a pyranometer will be especially helpful for such studies. He will want accurate readings from the pyranometer. 

\subsection{Design and Stakeholder concerns}
The main concerns are cost to build, easiness to build, and accuracy of data. One of the main purposes of the open-source pyranometer is to have it be cheap and easy to build by anyone with access to a 3D printer. Researchers and scientists should be able follow the documentation for the pyranometer and construct it without any headache. The data reported by the pyranometer needs to be reliable, otherwise it is useless. A fourth concern is the pyranometer's surviveability; the pyranometer needs to be weatherproof and the power source needs to last at least a few weeks.

\subsection{Design Viewpoint Descriptions}
\subsubsection{Black Body Object}
The black body object is what the thermopile senses in order to report the total solar radiation hitting the pyranometer. The object is meant the absorb solar radiation and emit IR radiation, which is detected by the thermopile and used to report the total solar radiation hitting the pyranometer.

\subsubsection{Power Source}
The power source is what supplies power the pyranometer. The power supply must be wireless and be able to sustain the pyranometer for weeks at a time.

\subsubsection{Data Transmission}
Data transmission refers to how the pyranometer wirelessly sends data back to the user. It is assumed that the user has a data hub or receiver that the pyranometer sends data to.

\subsubsection{Data Logging}
Data logging is how data from a sensor can be recorded. In this case, it refers to logging data manually for testing sake.

\subsubsection{Housing Structure}
The housing structure is the 3D printed object that will contain all other parts of the pyranometer to make it one sensor. 

\subsubsection{Weatherproofing Housing Structure}
Weatherproofing the housing structure refers to keeping the pyranometer safe from the elements. These include rain, water, and wind. 

\subsubsection{Analog Translation}
Analog translation is the method of converting the data gathered by the sensor in to usable data. For our project, we want the data to be converted into units $W/m^2$.

\subsubsection{Light Diffuser}
The light diffuser will be used to assist the sensor. It will evenly spread light onto the sensor to give consistent and acurate data.

\subsubsection{Dome Structure}
The dome structure is the material used to protect the light diffuser and sensor. It will be transparent to allow light to pass through and needs to meet weatherproofing criteria.

\section{Project Identification}
\subsection{Date}
The pyranometer project was assigned to the group on October 8th, 2018. It will end on the Engineering Expo hosted by Oregon State University in May, 2019. 

\subsection{Scope}
The pyranometer will be able to measure solar radiation and convert it to $W/m^2$. It will then transmit that data to a Google spreadsheet using the LOOM architecture. The goal of this project is to create an open-source and low-cost pyranometer that is comparable to an industry standard.  The project will also be open-source by adding any code added to the LOOM system on GitHub. All of the technology used to create the pyranometer should be available to any other lab or Maker Space. It should be able to be recreated with a 3D printer and access to funds to buy a few low-cost electronics. The benefit of creating something open-source is that it can be built all over the world. This is helpful because measuring solar radiation is good information around the globe. One use for this sensor is to use it for agriculture. Plants need sunlight to survive and using a pyranometer to know how much sunlight a particular area is getting is good information.

\subsection{Issuing Organization}
OPEnS lab is the primary sponsor of the wireless open-source pyranometer project, with Dr. Chad Higgins supplying the idea of the project. Once the project is complete, the pyranometer will become a part of the OPEnS collection of open-soure sensors.

\subsection{Authorship}
The authors and editors of this project are Brooke Weir, Garen Porter, and Alejandro Tovar. Suggestions, guidance, and recommendations made by Dr. Chad higgins and Dr. Chet Udell have influenced design decisions and edits made to most written documents for the pyranometer project. 

\subsection{Context}
There is a need for an open-source pyranometer that is wireless and well documented. Existing open-source pyranometers are either poorly documented or wired, so researchers who are looking for an open-source pyranometer that is well documented and wireless have no options. The wireless open-source pyranometer project will fill this need and look to serve researchers who need a cheap, wireless, and easy to assemble pyranometer. Most wireless pyranometers are expensive, and the open-source nature of this project serves will make the pyranometer much cheaper (only cost of materials and assembly need to be accounted for).

\section{Design Views}
\subsection{Black Body Object: Painted 3D Printed Dome}
Thermopiles, which is what is going to be used to report $W/m^2$ data, is a device that reads the temperature of an object using a die with a known temperature. More precisely, the thermopile reads the IR emanated from an object to calculate the object's temperature. To get accurate readings, black objects with high emissivity values need to be used. 
\subsubsection{Design Concerns}
The first concern is material cost and availability. Ideally, a cheap object with high emissivity should be used. The first material that comes to mind is Teflon, which is cheap and has an emissivity value of 0.92 (fairly high). Teflon, however, leads to the second concern; the object's ability to be shaped and formed. Teflon is a hard plastic that can only be shaped by a laser cutter and is not easily formed into shapes other than a sheet. Thermopiles work best when pointed at an infinite plane, and the best way to implement an infinite plane is to place the thermopile inside a dome, where the dome is the black body object. It may be possible to form Teflon into a dome shape, but it would be exceedingly difficult. An alternative, and what is now perceived as the best option, is to 3D print a dome out of Polyactic Acid (PLA) and paint the dome with Black 2.0. PLA is a popular plastic in 3D printing and its surface is able to be painted. PLA is inexpensive and 3D printing a dome structure will be easy and the dome can be made with any desired dimensions. Black 2.0 is the blackest and mattest paint available for purchase. A tube is about \$20 and will make the emissivity of the PLA about 0.99.\\A third concern is the accuracy of the data; which is directly related to the emissivty of the black body. The higher the emissivity of the object the higher the accuracy of the data. The emissivity of black PLA is about 0.92, but when the PLA is coated with Black 2.0 the emissivity increases. The emissivity of PLA by itself is high enough to where a user would not \textit{have} to paint it, but it would be best if users did use Black 2.0 to paint the PLA.
\subsubsection{Design Elements}
There are three required elements for the optical black object; a coil of black PLA; a 3D printer; a tube of Black 2.0; and a CAD design of the dome. The CAD file will be used to tell the 3D how to construct the dome. Once the dome is finished printing, it must be painted with Black 2.0 to achieve the highest emissivity possible. There needs to be a small slit on one side of the dome that allows the wires coming from the thermopile to pass under. The dome will be glued to the base of the housing structure with the thermopile inside. The dome should simulate an infinite black plane that allows the thermopile to get the most accurate readings possible. 
\subsubsection{Design Relationships}
The black object directly effects the thermopile and the housing structure. The dome is glued to the base of the housing structure and it must fully encapsulate the thermopile. The optical black object is a crucial element in ensuring accurate data is read from the thermopile.
\subsubsection{Design Rationale}
Ideally, an infinite plane with an emissivity value of 1 would be used as the optical black object. A dome surrounding the thermopile will accurately simulate an infinite plane, and coating black PLA with Black 2.0 will give as high an emissivity value as possible at a reasonable price. This approach to the optical black object should result in the most accurate data readings possible.

\subsection{Power Source}
A large part of this pyranometer project is to make it wireless, which primarily means that the pyranometer must have a wireless power source. There are several different possible routes to go, and different users may have different preferences. For the OPEnS open-source pyranometer, lithium batteries will be used, but the documentation will mention possible alternatives (solar panel, generators, etc.). 
\subsubsection{Design Concerns}
The main concern with the power source is how long it will last. The power source itself is the main factor in battery life, but the efficiency of the code in the microcontroller and how many sensors are connected to the microcontroller must also be considered. The current design has two thermopiles and a LoRa radio chip being connected to the Feather M0 microcontroller. All three of these take little power. LoRa is not power intensive by nature, and the thermopile sensors take readings every few seconds and are put in a low power state between taking readings.\\It was decided that lithium-ion batteries would be used to power the pyranometer. An initial concern was ease of use, and it is very easy to hook up a lithium batter pack to a Feather M0 (as simple as plugging a wire into a pin). Other implementations, such as a solar panel or thermoelectric generator, had a much more involved setup. The OPEnS lab already has lithium battery packs purchased, so no additional money needs to be spent on lithium batteries. For users outside the lab, the battery packs will cost between \$50 and \$75 dollars, but they are rechargeable and should last several weeks or months. There is a large discrepancy between the low end and high end of the estimated life of the batteries. This is due to the code efficiency playing a large role in how long the batteries will last, and it is difficult test the code's effect on the battery without deploying the pyranometer to the field and timing how long it lasts. 
\subsubsection{Design Elements}
For the power source there is only one design element, and that is the battery pack itself. The pack that OPEnS lab uses is a collection of six "AA size" lithium batteries. Other OPEnS projects reportedly last a couple months per charge, but it varies depending how well the code is written and how many sensors are a part of each project. The batteries are rechargeable and have a relatively low discharge rate (meaning not much charge capacity is lost per recharge) and can be recharged a few hundred times before needing to be replaced. 
\subsubsection{Design Relationships}
The project as a whole will not work without a power source, but the power source itself only effects the Feather M0 microcontroller and the housing structure. The housing structure needs to adequately protect the lithium batteries from any form of weather, and any heat coming from the batteries needs to be isolated from the optical black object. This entails the lithium batteries being enclosed by walls. The power source needs to adequately supply power the Feather M0 so that it may perform its functions for long periods. As long as the lithium batteries keep the Feather M0 running for long periods of time and the lithium batteries are adequately protected; the batteries are performing their job.
\subsubsection{Design Rationale}
Various power sources were judged based on three criterion; cost, ease of use, and average life. Lithium batteries are expensive initially, but can be reused over and over, so the overall cost is relatively low. Lithium batteries are long lasting in two senses; each charge of a lithium battery pack lasts a long time and the batteries can be reused over and over giving them a long overall life. Finally, lithium batteries are easy to use; simply plug them into the Feather M0 to power it, and plug them into a charging station to charge them. The pyranometer documentation will recommend a battery pack to buy, so users should be able to order the batteries and begin using them immediately. The housing structure will have an enclosure to set the battery pack in, with the goal of the enclosure being minimizing the heat impact of the batteries. The ease of use, longevity, and value of lithium batteries make them the ideal design choice for the pyranometer project.

\subsection{Data Transmission: LoRa Radio}
The purpose of using LoRa radio with the pyranometer is to wirelessly transmit data over long distances. LoRa is a wireless communication technology that consumes low amounts of power while being able to transmit data or long distance; the caveat is that LoRa operates under low bandwidth, thus limiting the amount of data that can be sent.
\subsubsection{Design Concerns}
There are several concerns when implementing LoRa radio, first of which is keeping power consummation low. LoRa, by nature, consumes low amounts of power compared to other data transmission methods (Wifi and Cellular), but to further assist with power consumption the \textit{rocketscream/Low-Power} Arduino library will be used. The library assists with power management by frequently putting the Feather M0 in a lower power mode.\\A second concern is keeping the pyranometer structure weatherproof. Using LoRa radio requires use of an external antennae, which means that an antennae needs to protrude out of the housing structure. To make this protrusion possible, a hole will need to made in the housing structure. The hole will need to be just wide enough to fit the antennae, and a resin will be applied around the hole to help seal the crack between the antennae and the housing structure.\\A third concern is fitting the LoRa transmitter chip neatly inside the housing structure. Within the housing structure, there will be the Feather M0 microcontroller attached to a multiplexer, two thermopile sensors, a lithium battery packet, the LoRa radio chip, and two black body objects. All of the hardware needs to fit inside as small of a structure as possible and not interfere with the readings from the thermopiles. To limit interference, there will need to be a barrier between the black body object and the LoRa chip (any source of external heat will interfere with the black body temperature). The housing structure is going to be 3D printed, so thin 3D printed barriers will be made between each chip, and the LoRa radio chip will be placed on the edge of the inside of the structure. An SMA connector will be facing the inside of the outer wall of the structure, thus allowing the antennae to be easily screwed in from the outside. 
\subsubsection{Design Elements}
The physical chip that will be used is an \textit{Adafruit RFM95W LoRa Radio Transceiver} along with a SMA connector to allow an antennae to be securely connected to it. The chip will be connected to a multiplexer that will be connected to a Feather M0 (the microcontroller controlling the pyranometer and making all computations). The chip itself is about the size of a quarter, and the antennae and SMA connector take up no space inside the housing structure.\\The \textit{LOOM LoRa API} will be used to setup and configure the LoRa radio with the pyranometer. The API has implementations for receiving and sending OSC bundles (data packets containing sensor readings). The LOOM LoRa API makes use of the following APIs and libraries: \textit{adafruit RadioHeaad, GreyGnome EnableInterrupt, FabioCuomo FabioCuomo-DS3231, rocketscream Low-Power, CNMAT OSC}, and \textit{EnviroDIY Arduino-SDI-12}. Each library is made specifically for use by Arduino microcontrollers, and each library assists or enhances the LoRa radio implementation. 
\subsubsection{Design Relationships}
The wireless transmission, both the non-physical and physical aspects, relate to the housing structure, black body objects, and Feather M0. The housing structure will need to have a wall between the LoRa chip and the black body object to limit interference. The housing structure will also need a hole cut where the radio antennae needs to poke out of. The Feather M0 will need to be configured to send data packets over LoRa radio to a LoRa receiver. The LOOM API has a configuration file that will need to set to use LoRa. With the configuration file correctly configured, the thermopile readings will need to be organized into OSC packets (this is all done by the API). The only code that will need to be written is a call to the LoRa send function (the function will be called in the main loop every few seconds). 
\subsubsection{Design Rationale}
LoRa radio is the best option for data transmission due to its low power consumption and high range. There is an existing API already implemented in LOOM to make LoRa easy to implement. Many other OPEnS IoT devices usu LoRa as well, so there are LoRa receivers already set up and there are examples to follow. As long as the housing structure is designed carefully, the weatherproofing and data interference concerns can be negated.

\subsection{Data Logging: Adalogger}
LOOM will be used to log data from a sensor onto either a spreadsheet or a micro SD card. When configuring the LOOM system for the pyranometer, LOOM can either put the recorded data on a micro SD card or transmit it to a Google spreadsheet. To upload to a Google spreadsheet, the pyranometer will use LoRa radio which was covered earlier. In this section, the SD card route using the Adafruit Adalogger will be examined. 

\subsubsection{Design Concerns}
The major concern with the Adalogger is that the information recorded on the SD card will have to be manually taken from the sensor and onto a computer. Having to manually move the data will not be helpful for a sensor since they are meant to be left outside for a long period of time without human involvement. Also an SD card can only hold so much data. The SD card will mostly be involved during the testing of the sensors so the concern is valid, but the SD card will not be involved in the final prototype.

\subsubsection{Design Elements}
The Adalogger can be hooked up to a multiplexer that is also connected to the Feather M0 and a sensor. The Adalogger can take the data from the sensor and put it on a micro SD card. The micro SD can then be taken out and put into an SD card. The files on the SD card can then be read from a computer. 

\subsubsection{Design Relationships}
The Adalogger will be connected to the multiplexer and Feather M0. The multiplexer is what connects the sensor to the Feather M0 and Adalogger. The Adalogger will take the data that the sensor gets and put it on a micro SD card. 

\subsubsection{Design Rationale}
The purpose of the Adalogger is to give a quick way to get data from a sensor for testing. Testing is an important part of making sure that the data the pyranometer senses is accurate. Using the Adalogger is a good way to get the data and determine if it is correct. 

\subsection{Housing Structure: A 3D Printed Design}
The housing structure will enclose the electronics for the pyranometer such as the sensors, a LoRa radio chip, and others. It will be 3D printed with a space for an antennae to poke out. 

\subsubsection{Design Concerns}
A concern for the housing structure is to fit all the electronic pieces within the structure while not cramming the electronics too closely. This is important so that the sensors do not pick up heat from other electronics such as the battery pack or LoRa radio chip. The Feather M0, LoRa radio chip, and any other electronics will have to maintain some distance from the black bodies and sensors. Otherwise the data will not be accurate.\\
Another concern is the hole where the LoRa antennae will poke out of the structure. It leaves a space in the housing structure where the elements can affect the electronics more easily. Rain or wind can enter the structure and screw the data as well as create damage. The resin applied to the 3D printed structure should prevent such damage from happening, but the antennae does leave room for error. 

\subsubsection{Design Elements}
The housing structure will be 3D printed and then coated with a resin. To create the structure, CAD will be used to create the design and one of the three 3D printers available at the OPEnS lab will be used to print it. The structure will then be coated in a resin to help weather proof the design. The antennae for the radio will be added to the housing and have a resin applied to minimize the space where the elements can enter the pyranometer. 

\subsubsection{Design Relationships}
The housing structure has a relationship with all other components of the pyranometer since it will contain all of them. All of the parts of the pyranometer, except the radio antennae, will be contained within the housing structure. The radio antennae will be partially enclosed in the structure.

\subsubsection{Design Rationale}
The purpose of the housing structure is to have something to surround all of the electronics so each unit is portable. It is there so that there are not loose electronic pieces. The housing structure also protects the electronics from the elements. The housing structure allows the components to be put together and called one single sensor. 

\subsection{Weatherproofing Housing Structure: 3D Printing and a Resin}
Weatherproofing the housing structure for the pyranometer is important to protect the electronics and to obtain accurate data. The structure itself will be 3D printed with a LoRa radio antennae sticking out of the structure. The structure will have to be protected from the elements as well as insulated to get accurate, reliable data. 

\subsubsection{Design Concerns}
There are several concerns for weatherproofing the housing structure for the pyranometer. The first concern is to prevent water damage on the sensor inside the housing. Water damage can seriously damage the technology. There will be some areas where the possibility of water damage will be higher. One such area is where an antennae will protrude out of the housing structure for the LoRa radio. Preventing water damage is crucial to keep the battery, Feather M0 working, and other electronics working. Another concern with waterproofing the housing structure is to protect the sensors that depend on heat to read data. Heat comes from the sunlight coming in, but also wind and ambient heat affects the temperature. The housing structure should be insulated from wind and other types of heat. 

\subsubsection{Design Elements}
The housing structure will be 3D printed. There are ways to 3D print the housing structure to make it more waterproof. The first way to do so will be to print the thick layers [4]. This will reduce the overall amount of layers which will decrease the areas that water can slip through between layers. The second way to do so will be to print the housing structure will 100\% infill [4]. The third way to do so will be to print several perimeters to enclose the electronics. Having smaller structures enclosed within another structure will add to the number of layers water will have to go through to damage the electronics. It can also help insulate the electronics from wind and heat.\\
Beyond 3D printing the structure in particular ways, another way to weatherproof the housing structure is to apply a resin. Applying a resin to the 3D printed structure will fill in the gaps between the layers. The resin itself will be resistant to the elements and help the overall structure from being damaged. 

\subsubsection{Design Relationships}
Weather proofing the housing structure has a relationship with everything inside the structure. It will have to protect everything inside from wind, rain, and ambient heat or lack thereof. Specifically, weather proofing will interact with the LoRa radio antennae since the antennae will have to protrude outside of the housing structure. Otherwise, the housing structure will protect the Feather M0, two thermopile sensors, a battery, a LoRa radio chip, and two black body objects. 

\subsubsection{Design Rationale}
The purpose of weather proofing the housing structure is to protect the electronics from the elements such as wind, rain, and heat. This is necessary to keep the pyranometer running. Each component, aside from the black body objects, inside the structure will be small electronics. Those pieces will be susceptible to water damage. Protecting against wind and heat will protect the electronics from experiencing extreme temperature fluctuations as well record accurate data.

\subsection{Analog Translation}
Analog Translation is the process of converting solar radiation into some form of usable data. For this project we want to be able to read in solar radiation as $W/m^2$. The micro-controller needs a way to achieve this translation. There are some hardware that can simplify this task, but can be expensive. For our purpose, using open source software and modifying it for our needs will be best suited for this project.
\subsubsection{Design Concerns}
The written and modified code will need to be simplified and well documented for other users to understand. Once we can get our code to compile and translating data, we will need to run tests to determine the accuracy of our translations. The code will also need to be compatible with the chip if the micro-controller and to maker sure we don't overwork the chip with the program.
\subsubsection{Design Elements}
The micro-controller will be programmed with our translator to read in data as heat. Then using a physics equation that will need to be derived, the program should be able to take in the data the micro-controller is reading and convert it into data with units $W/m^2$. The data will then be ready to be sent and logged on a spreadsheet.

\subsubsection{Design Relationships}
The design of this program will be compiled and downloaded onto the chip of the micro-controller to perform it's calculations. It will get the data that was gathered from the sensor and convert it into our desired data in $W/m^2$ units.
\subsubsection{Design Rationale}
Using open source software is better for this project because it is being integrated into an open source data hub. The goal of the project is to get a solar radiation sensor onto the Loom git hub repository for others to use. It is cheaper than having to buy dedicated hardware that can do this translation for us. 

\subsection{Light Diffuser}
The light diffuser is a piece of material that will spread light evenly onto the sensor. This part of the device plays an important role in the accuracy of our sensor. The light transmittance efficiency of the diffuser will play a big role in the design of this part. The light transmittance efficiency is a rating of how much light passes through an object.
\subsubsection{Design Concerns}
Some concerns will be material of the diffuser and the thickness. It needs the right amount of light transmittance.  The sensor is like the human eye, too much light and it will be blinded by bright light, but too little light and it will be difficult to see. We need the right amount of light to pass through our diffuser. We don't want to overstimulate the sensor or not have enough. The material will determine how much light and what kind of light can get through. Thickness will also determine how much light will pass through. Price of the material is also a concern that will need to be taken into account.
\subsubsection{Design Elements}
Our ideal diffuser will have a surface called a Lambertian surface. A Lambertian surface is the ideal surface for diffusing light. The idea is that the brightness of light is the same regardless of the observer's angle view. If our diffuser has this kind of effect, then we can evenly distribute light for an accurate reading. We plan on using our diffuser as both a diffuser and to play small role in protecting our sensor. The diffuser will be dome-like to account for all angles of sunlight.
\subsubsection{Design Relationships}
The diffuser will have to be big enough to cover our sensor. This is to get the most out of the sensor. It will also have to adhere to the housing structure as well. We will have to make sure that this piece maintains our goals of weather proofing the device.
\subsubsection{Design Rationale}
The diffuser needs to be able to distribute light as even as possible to give our sensor enough data. It will also need to let in the right amount of sunlight so the sensor doesn't get overstimulated or have to little to work with. A dome size structure is needed to cover the sensor as well as to fit in the housing structure design. White diffusing glass will be used as it has a good light transmittance that can adjusted by adding layers of glass to increase or decrease thickness.

\subsection{Dome Structure}
The dome structure is what will overall protect the sensor as well as the diffuser. It will need to be durable and be able to let sunlight in. As well as meet the weather proofing goals since it is an outer layer of our device. For the dome structure, the material will be made out of acrylic plastic. 
\subsubsection{Design Concerns}
Some concerns include cost, durability, and light transmittance efficiency. The material used will need to have a low cost to keep our device from being too expensive. The material will also have to be durable to survive long periods of time in any environment it is use in. Since this will cover our diffuser, we need to maker sure light can pass through and enough light passes through to the diffuser. This will play a role in the accuracy of the sensor.
\subsubsection{Design Elements}
The dome structure will be bigger than the diffuser in order to cover and protect it. The material will be acrylic. The dome structure will have the same shape as the diffuser to for this design. 
\subsubsection{Design Relationships}
The dome structure is used to protect the diffuser and the sensor. It will need to fit with the housing structure as well. Since it is a part of the housing structure it will need to be weather proof just like the rest of the structure.
\subsubsection{Design Rationale}
Acrylic material will be used for this dome structure. It is more durable than glass, and less heat conductive. This is important because the sensor will read in heat, and any external heat can lead to errors. Acrylic is also cheaper than other viable materials, making it the better choice in terms of cost. The material also has a high light transmittance and lets in the most amount of different wavelengths of sunlight. The sensor needs to read in UV, Infrared, and the visible spectrum so acrylic is the ideal choice.

\section{Conclusion}
\begin{figure}[h]
\centering
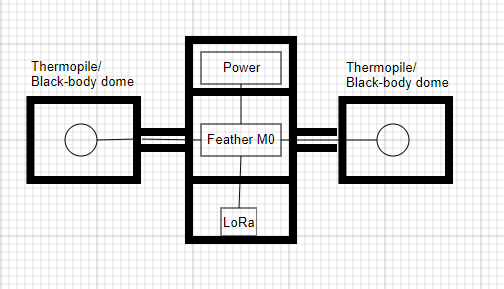
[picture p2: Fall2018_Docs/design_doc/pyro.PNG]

\caption{Top-down design of the open-source pyranometer.}
\end{figure}
Figure 1 shows the current design of the open-source, wireless pyranometer. The design is heavily influenced by various design concerns, such as data accuracy, cost, and ease of assembly. Each hardware piece is put behind a 3D printed wall, and the thermopiles (and surrounding black-body dome) are put behind two walls to limit any excess thermal energy from interfering with the thermopiles' readings. Each wall will have a small slit for wires to go through, but each hardware piece should otherwise be separate from each other. Having different "compartments" for each hardware piece should make assembly easier, as users will simply need to place each hardware piece in its respective slot. The entire structure, as well as the domes surrounding the thermopiles, will be 3D printed to limit cost. A second 3D printed structure will be placed over the top of the base to protect the hardware from the environment in order to keep it weatherproof.\\\\
A common theme throughout the various designs is keeping pyranometer safe in the field (deployed in the environment) and ensuring the data it reports is accurate. All of the OPEnS sensors are meant to live out in various climates and the pyranometer is no different. In each design decision, weatherproofing and data accuracy were considered to help ensure that the pyranometer is reliable in most environments. Besides keeping the pyranometer weatherproof and ensuring accuracy of data, ease of assembly and price are two important factors considered in each design decision. Everything that can be 3D printed is being 3D printed to keep cost down and make assembly easier. For the parts that cannot be 3D printed, such as the top domes, the best value parts are chosen. The design decisions made should lead to a pyranometer that can survive in most environments, be easy to assemble, be inexpensive (relative to other wireless pyranometers), and produce reliable data.

\section{Glossary}
\textbf{Black 2.0}: \textit{The blackest paint available to the public; created by Stuart Semple and inspired by Vantablack [1].}\\\\
\textbf{Emissivity}: \textit{An objects ability to emit thermal radiation (IR).}\\\\
\textbf{Feather M0}: \textit{A small, lightweight microcontroller developed by Adafruit.}\\\\
\textbf{Infrared (IR)}: \textit{A form of electromagnetic radiation emitted from heated objects.}\\\\
\textbf{Lambertian Surface}: \textit{ A quality a transparent object may have. Where the brightness of light passing through is the same in any angle it is viewed at. This is regarded as an ideal diffuser}\\\\
\textbf{Light Diffuser}: \textit{An object that can evenly distribute light passing through on a surface.}\\\\
\textbf{Light Transmittance Efficiency}: \textit{A rating on the percentage of light that can pass through an object.}\\\\
\textbf{Lithium-ion battery}: \textit{A rechargeable battery that generates electricity via the movement of positively charged lithium ions.}\\\\
\textbf{Long Range (LoRa)}: \textit{A wireless communications technology developed by Semtech [2]}\\\\
\textbf{LOOM}: \textit{An IoT system designed by the OPEnS lab. It seeks to make the process of creating IoT devices simple.}\\\\
\textbf{Pyranometer}: \textit{A device that detects solar radiation and reports the total solar irradiance in $W/m^2$.}\\\\
\textbf{Open-source}: \textit{Refers to software and code being freely available to the general public.}\\\\
\textbf{Openly Published Environmental Sensing (OPEnS)}: \textit{An organization sponsored by Oregon State University dedicated to creating open-source environmental sensors using modern technology.}\\\\
\textbf{Resin}: \textit{A material that is insoluable to water.}\\\\
\textbf{SD card}: \textit{A type of portable memory card.}\\\\
\textbf{Thermopile}: \textit{A device that converts thermal energy (IR) into electrical energy (volts) and reports the temperature of an object.}\\\\
\textbf{3D Printing}: \textit{A method of layering plastic into a three dimensional object based on a model.}\\\\

\section{References}
{[}1] S. Cascone, “Vantablack vs. Black 2.0: Which Is the Superblack for You?,” \textit{artnet News}, 30-Mar-2017. [Online]. Available: https://news.artnet.com/art-world/vantablack-vs-black-superblack-907556. [Accessed: 03-Nov-2018].\\
\\{[}2] n.a, "Introduction to LoRa Technology – The Game Changer", \textit{Maker.IO}, 10-Aug-2016. [Online]. Available: https://www.digikey.com/en/maker/blogs/introduction-to-lora-technology\\
\\{[}3] Adafruit Feather M0 Adalogger. \textit{Adafruit}. [Online]. Available: https://www.adafruit.com/product/2796. [Accessed on November 20, 2019].\\
\\{[}4] Stevenson, K. Waterproofing Your 3D Prints, \textit{Fabbaloo}, October 19, 2017. [Blog]. Available: https://www.fabbaloo.com/blog/2017/10/19/waterproofing-your-3d-prints. [Accessed on November 2, 2018]. \\

\end{document}

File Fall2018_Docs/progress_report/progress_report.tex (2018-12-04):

\documentclass[10pt,draftclsnofoot,onecolumn,letterpaper]{article}
\usepackage{ragged2e}
\usepackage[svgnames,table]{xcolor}
\usepackage[hidelinks]{hyperref}
\usepackage{listings}
\usepackage{graphicx}
\usepackage{longtable}

\usepackage[utf8]{inputenc}
\usepackage[left=0.75in, right=0.75in, top=0.75in]{geometry}
    
\usepackage[T1]{fontenc}
\setlength{\parindent}{0pt}

\begin{document}
\begin{Center}
{\fontsize{14pt}{16.8pt}\selectfont OPEnS Pyranometer: IoT Solar Radiation Sensor\\ Progress Report\par}
\end{Center}\par
    
\begin{Center}
Garen Porter, Brooke Weir, Alejandro Tovar\\
\end{Center}\par
\hrule
\begin{Center}
{\fontsize{12pt}{16.8pt}\selectfont \textbf{Abstract}\par}
\end{Center}\par
    
{\fontsize{10pt}{12.0pt}\selectfont Over the course of the fall term, the Pyranosaurs team has done substantial research into pyranometers and the various parts that they consist of. We have explored several different technologies and have come up with the most optimal implementations for the wireless, open-source pyranometer we plan to implement. We have kept in mind various criterion throughout the term and have gotten to the point were we are now ready to begin building and implementing a couple different pyranometer designs.
\par}\par
\newpage
\pagenumbering{arabic}
\tableofcontents
\clearpage
    
\section{Goals}
    The goal of the Pyranosaurs team is to make an IoT solar radiation sensor that is open-source, low-cost, accurate, and easy to assemble. Open-source pyranometers exist, but they are poorly documented and not wireless. To keep the pyranometer low-cost, the parts used will either be inexpensive or 3D printed. To make the pyranometer open-source, the CAD designs and code will be freely available online to give users the ability to construct the pyranometer anywhere with access to a Maker Space. Instructions to build, operate, and deploy the pyranometer will be thorough and easy to follow to make the pyranometer as user friendly as possible. As the pyranometer project progresses, it will continually be tested against commercial-grade sensors to verify accuracy. Due to the pyranometer project being sponsored by the OPEnS lab, it must successfully integrate into the LOOM IoT system and follow the same protocols as the other OPEnS lab projects. As with other OPEnS projects, the pyranometer will be wireless. To do this, the pyranometer will transmit data via LoRa radio to a data hub that will use a PushingBox API that translates the data into HTTPS and uploads the data to a Google sheet.
    
\section{Current State}
Currently, we have a physical design finished for the thermopile and photo diode pyranometers. We are waiting for several parts to arrive so that we may implement the photo diode pyranometer. The thermopile pyranometer design consists of mostly 3D printed parts, so we are ready to begin creating CAD designs for the thermopile pyranometer. We have tests written and designed to begin verifying and calibrating the thermopile, so we can begin performing those tests any time. Each team member has done thorough research on pyranometers in general and on their respective pyranometer parts (as seen in our tech reviews), so we are about ready to start building and implementing designs.
\section{Problems and Solutions}
Our first and biggest problem is waiting for parts to arrive. We ordered parts for a photo diode-based pyranometer a few weeks ago, but they have yet to arrive. We will be checking with our client and talk about expediting the shipping process, or see if something went wrong with the parts order. A second problem we are having is getting the thermopile to work with the multiplexer/Feather M0 combination. We will be working with the OPEnS staff and see what we are missing with the sensor integration and look into updating the LOOM documentation on how to integrate I2C sensors into LOOM.
\section{Interesting Code}
The below code segment is the setup function for the Adafruit TMP007, better known as the thermopile. The thermopile is registered under I2C address 0x41, which the multiplexer uses to interact with the thermopile. The delay value is the interval at which the thermopile takes readings, this value is adjusted per the thickness of the black body object being measured.
\begin{lstlisting}[caption={TMP007 Setup},captionpos=b]
bool setup_tmp007() 
{
    //Setup Here
    Serial.print("SETTING UP THERMOPILE\n");
	bool is_setup;
	state_tmp007.inst_tmp007 = Adafruit_TMP007(0x41);
	if(state_tmp007.inst_tmp007.begin()){
		is_setup = true;
		config_tmp007.delay = 4000;
		LOOM_DEBUG_Println("Initialized tmp007");
	}
	else{
		is_setup = false;
		LOOM_DEBUG_Println("Failed to initialize tmp007");
	}

    Serial.print("FINISHED SETTING UP THERMOPILE\n");
    return is_setup;
}
\end{lstlisting}

Listing 2 shows the thermopile taking measurements. The thermopile reports the local temperature of an object (the black body), the temperature of the thermopile die, and the voltage generated by the thermopile. After this function is called by the multiplexer, the data is packed into an OSC bundle and either written to an SD card or transmitted over a wireless protocol (Wifi or LoRa). 

\begin{lstlisting}[caption={TMP007 Setup},captionpos=b]
void measure_tmp007() 
{
  Serial.print("MEASURING\n");
	state_tmp007.volt = state_tmp007.inst_tmp007.readRawVoltage();
	state_tmp007.obj_temp = state_tmp007.inst_tmp007.readObjTempC();
	state_tmp007.die_temp = state_tmp007.inst_tmp007.readDieTempC();

  #if LOOM_DEBUG == 1
    Serial.print(F("[ ")); Serial.print(millis()); Serial.print(F(" ms ] "));
    Serial.print(F("Volts: ")); Serial.print(state_tmp007.volt); Serial.print(F("  "));
    Serial.print(F("Die Temp: ")); Serial.print(state_tmp007.die_temp); Serial.print(F("  "));
    Serial.print(F("Object Temp: ")); Serial.print(state_tmp007.obj_temp); Serial.print(F("  "));
  #endif

  Serial.print("DELAYING\n");
  delay(config_tmp007.delay);
}
\end{lstlisting}

\section{Week by Week Summary}
\subsection{Week 1}
Week 1 was about becoming familiar with senior capstone and knowing what to expect throughout the year. At this point no one knew what project they would be working on.
\subsection{Week 2}
Week 2 was similar to week 1, but at this point each student was trying to figure out which projects they would be interested in. 
\subsection{Week 3}
In week 3 we learned we would be working with Chet on building a wireless, open-source pyranometer. Each team member drafted a problem statement which were later combined into a single problem statement. We made contact with our client and set up a time to meet and discuss the project. We also made our group GitHub repository and met with our TA for the first time. 
\subsection{Week 4}
We first met our client during week 4 and we were able to discuss the project and work out different goals to strive for each term. Fall term was to be a time to develop three pyranometer prototypes; winter term is to involve testing the prototypes and seeing which implementations are best; and during spring we are to synthesize the three prototypes into a single pyranometer. We were introduced to Chad Higgins and set up a time to meet with him the following week. Finally, we finished our problem statement and submitted it.
\subsection{Week 5}
During week 5 we created a rough draft of our requirements document, ordered parts for two of our pyranometer prototypes, and met with Chad Higgins. During our meeting with Chad, we modified our time-line slightly and pushed back the due date for our three prototypes to halfway through winter term. Chad pointed out some potential difficulties we may encounter when implementing our different designs. We as a team came up with 3 parts for each team member to focus on for our tech reviews and for the rest of the year. Each team member was to become an expert on their assigned parts. We also started to familiarize ourselves with some of the equipment we would be using for our pyranometer. We started by making a Feather M0 blink an LED to get started working with Arduino products. 
\subsection{Week 6}
During week 6 we submitted our requirements document to our client and he gave us some helpful feedback. As a team, we sat down and wrote a document that outlines the expectations we have of each other and as a team. We began writing our respective tech review documents and each began researching pyranometers, thermopiles, and photodiodes heavily. We began working with a lux sensor and were able to program a Feather M0 to get record readings from the lux sensor and write them to an SD card. The lux method is to be one of our pyranometer designs, so this week we essentially finished the hardware portion of the lux-pyranometer design. The lux sensor was already integrated into LOOM, so it was a good experience to familiarize ourselves with how a LOOM sensor should work as a baseline. 
\subsection{Week 7}
Our thermopile arrived week 7 and we were able to solder pins to it and wire it to a Feather M0. We were able to get readings from the thermopile via the serial monitor in the Arduino IDE. We reached to Chad Higgins to setup a meeting with him about how to verify the accuracy of the thermopile and how to translate the thermopile data to $W/m^2$. We each finished our tech reviews this week.
\subsection{Week 8}
During week 8 we met with Chad Higgins and discussed the thermopile and photo diode methods in detail. We went over how they work, how to verify them, and how to create useful data from them. From the information gained in the meeting, we were able to refine our thermopile-based pyranometer design and create tests that verify the thermopile and photo diode methods. We began trying to integrate the thermopile sensor into LOOM, but were unsuccessful. 
\subsection{Week 9}
Week 9 was a short week due to Thanksgiving break. We began work on our design document, which entailed each of us discussing how we are going to implement the technologies and parts discussed in our tech reviews. 
\subsection{Week 10}
During week 10 we finalized and submitted our design document. We revised our requirements document using the revision recommendations made by our client. We created our fall term progress report (both the video and written portion) and submitted our design document, requirements document, progress report, and problem statement to our client for verification. We also created an experimental procedure for testing the thermopile based on Chad's input.

\section{Retrospective}
%\begin{center}
    \begin{longtable}{| p{0.17\linewidth} | p{0.22\linewidth} | p{0.22\linewidth} | p{0.22\linewidth} |}
         \hline \textbf{Task} & \textbf{Positives} & \textbf{Deltas} & \textbf{Actions} \\
         \hline Problem Statement & Completed. & None. & None. \\
         \hline Requirements & On second draft. & Continue to revise. & Change based on further comments from Chet. \\
         \hline Design Document & On first draft. & Continue to revise. & Make changes based on client feedback. \\
         \hline Feather M0 & Works with Adalogger and sensors; able to write sensor data to an SD card. & Be able to get readings from multiple sensors, be powered wirelessly, and transmit data over LoRa. & Connect feather to a multiplexer (Adafruit TCA9548A) and configure it to control multiple chips; wire a lithium-ion battery pack to the feather. \\
         \hline Lux sensor & Able to sense and put data on an SD card; integrated into LOOM. & Verify accuracy of reported data. & Test the lux sensor probably against standard IR sensor. \\
         \hline Thermopile & Able to Sense and output data to serial monitor. & Needs to be integrated into LOOM and work with a multiplexer. & Work with OPEnS lab staff on how to finish integrating the thermopile into LOOM. \\
         \hline Photodiode & We understand how the photodiode method works. & Need the parts to arrive; need to construct a photdiode based pyranometer. & Talk with our client and see about expediting the shipping process for hte photodiode parts.\\
         \hline LOOM & We understand the purpose and function of LOOM; we understand how new sensors can be integrated into LOOM. & Configure the thermopile to correctly integrate with the multiplexer. & Work with OPEnS staff to understand how the multiplexer communicates with attached chips. \\
         \hline Housing structure & Researched ways to create a good way to house all of the elements and get accurate data.  & Needs to be printed. & Create designs in CAD and print those designs in one of the 3D printers at OPEnS lab. \\
         \hline Weatherproofing & Researched ways to insulate against wind and protect the sensor from water damage. & Needs to be applied to structure. & Build the structure and apply ideas that have been researched. Test the housing structure for damage before putting electronics inside. \\
         \hline Black Body Object & The best black body object to use is a common 3D priting material & Create a black dome made out of PLA. & Design the dome using CAD and print it. \\
         \hline Power Source & The lithium-ion battery chosen to be used is the same power source used in many other OPEnS projects. & Make the pyranometer wireless & Wire a lithium-ion battery pack to the Feather M0. \\
         \hline LoRa Radio & Can be implemented easily with LOOM using the LOOM API. & Give the pyranometer the ability to trasmit data over LoRa. & Wire a LoRa chip to the Feather M0, attach an antennae, and usee LoRa LOOM API to trasmit data readings to a Google sheet. \\
         \hline
    \end{longtable}
%\end{center}

\end{document}

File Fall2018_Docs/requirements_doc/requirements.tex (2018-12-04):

\documentclass[10pt,draftclsnofoot,onecolumn,letterpaper]{article}
\usepackage{ragged2e}
\usepackage[svgnames,table]{xcolor}
\usepackage[hidelinks]{hyperref}

%\usepackage{pgfgantt}
\usepackage{graphicx}
    
\usepackage[utf8]{inputenc}
\usepackage[left=0.75in, right=0.75in, top=0.75in]{geometry}
    
\usepackage[T1]{fontenc}
\setlength{\parindent}{0pt}

\begin{document}
\begin{Center}
{\fontsize{14pt}{16.8pt}\selectfont OPEnS Pyranometer: IoT Solar Radiation Sensor\\ Project Requirements\par}
\end{Center}\par
    
\begin{Center}
Garen Porter, Brooke Weir, Alejandro Tovar\\
\end{Center}\par
\hrule
\begin{Center}
{\fontsize{12pt}{16.8pt}\selectfont \textbf{Abstract}\par}
\end{Center}\par
    
{\fontsize{10pt}{12.0pt}\selectfont The IoT solar radiation sensor, referred to as the pyranometer, is to be a wireless and open-source solar radiation sensor that integrates into the Loom architecture. The goal of this project is to create a completely open-source pyranometer that is comparable to commercial-grade pyranometers that can cost thousands of dollars. The pyranometer will be able to sense and record some combination of UV, IR, and visible spectrum solar radiation hitting the pyranometer and transmit the data to a remote data hub. The pyranometer will record accurate data, last weeks in the field on battery power, and be able to survive most climates.
\par}\par
    
\newpage

{\fontsize{12pt}{12.0pt} \textbf{1\quad Introduction}\\\selectfont 
\par}\par
{\fontsize{10pt}{12.0pt} \textbf{1.1\quad System purpose}\\\selectfont 
\par}\par
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

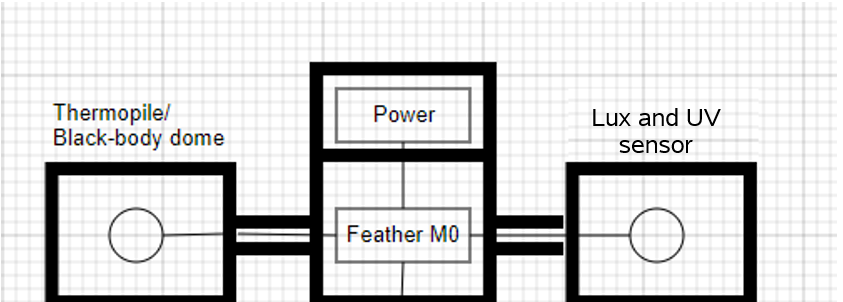
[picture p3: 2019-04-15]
Spring2019_docs/DesignDoc/images/pyro.PNG

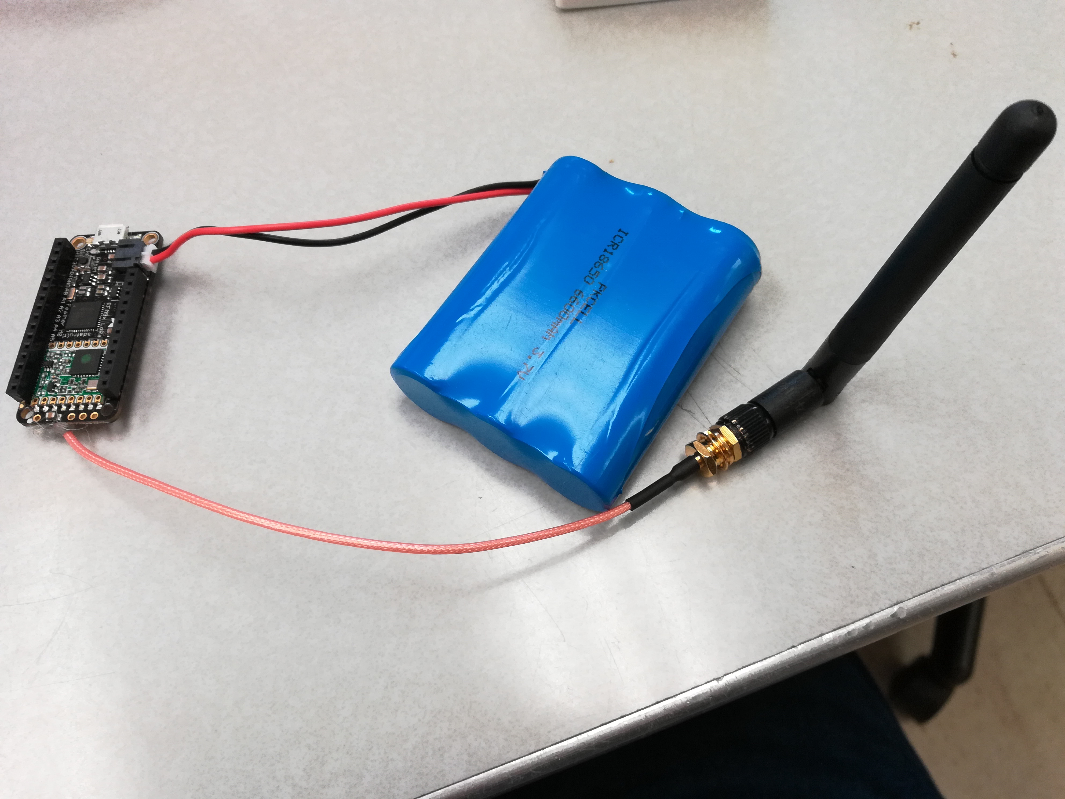
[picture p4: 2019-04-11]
Images/feather_wo_featherwing.jpg

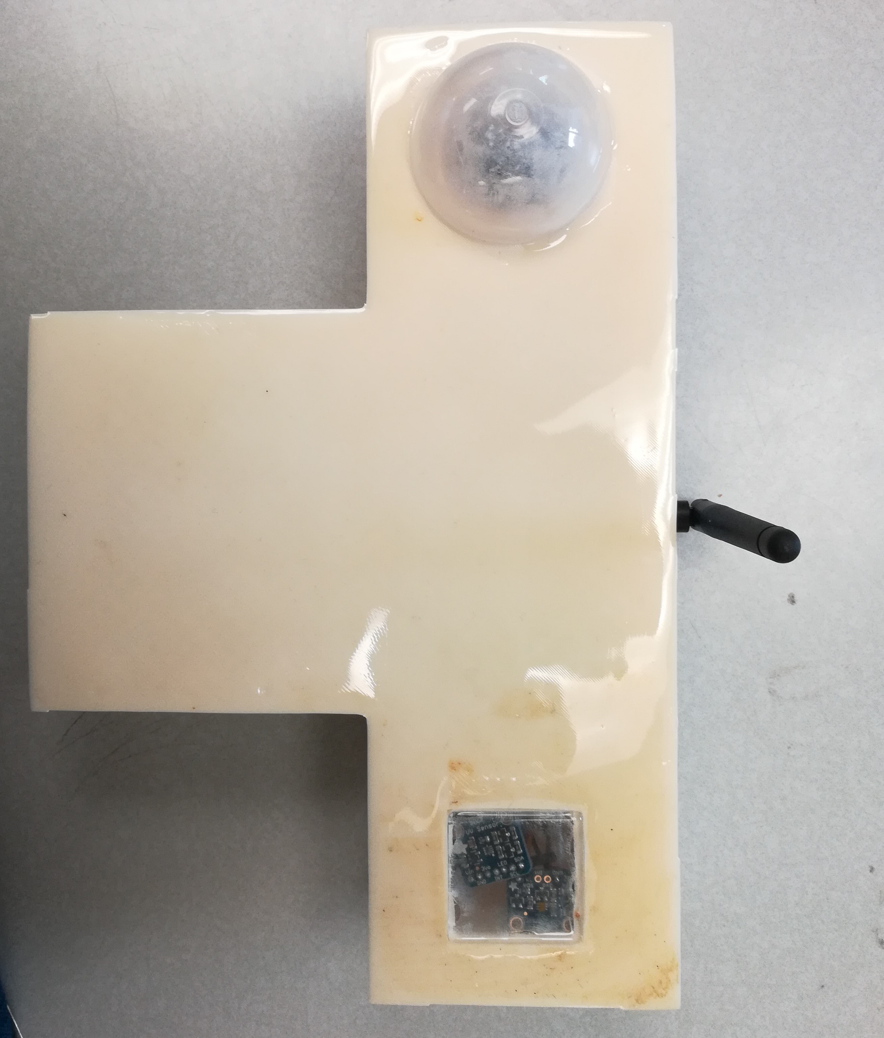
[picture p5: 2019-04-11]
Images/pyro_with_lid.jpg

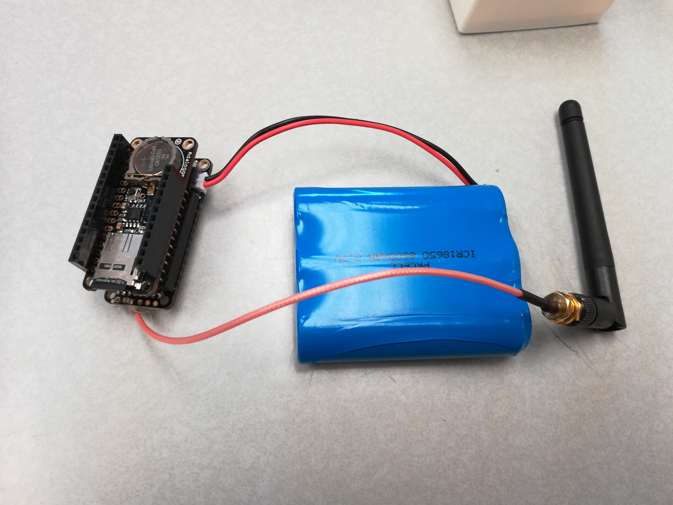
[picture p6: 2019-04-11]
Images/node_with_featherwing.jpg

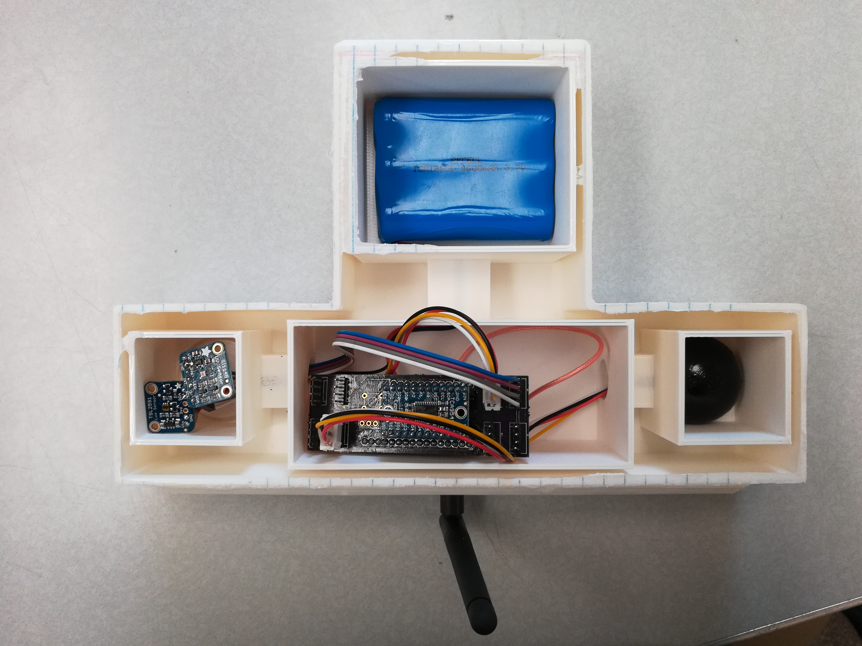
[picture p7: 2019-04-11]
Images/pyro_topview2.jpg

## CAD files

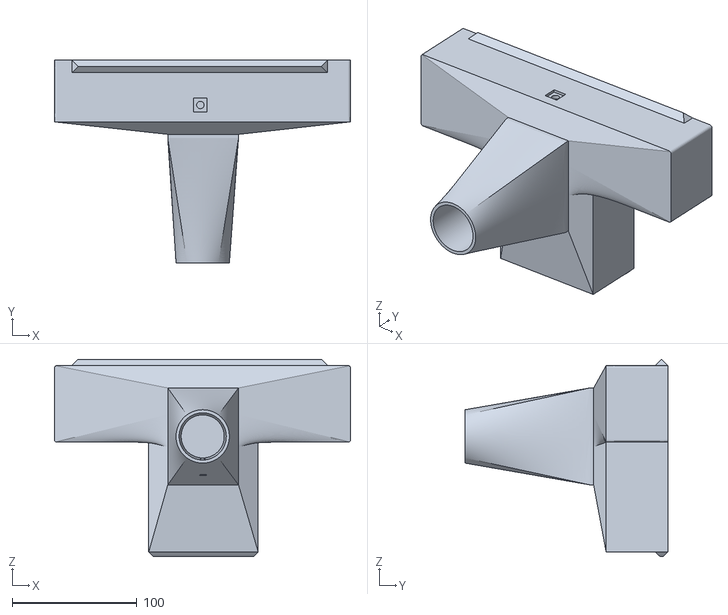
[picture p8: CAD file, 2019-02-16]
CAD/bottomHousing_withPole.stl
237.1 x 162.5 x 158.2

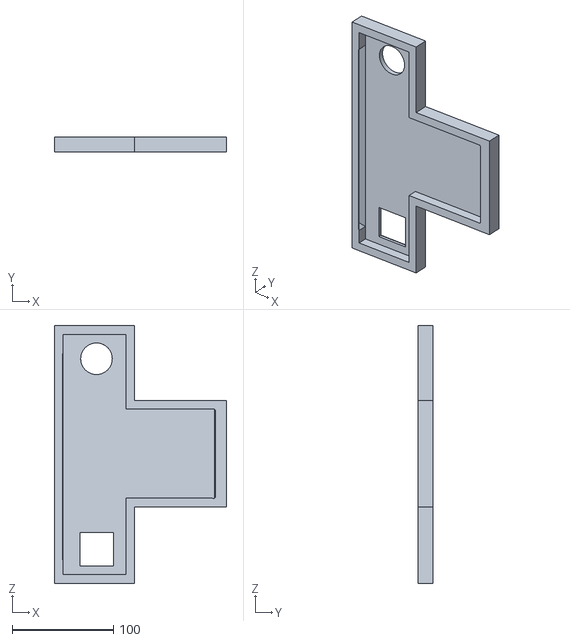
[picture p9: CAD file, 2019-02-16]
CAD/lid.stl
170.4 x 15.0 x 255.1

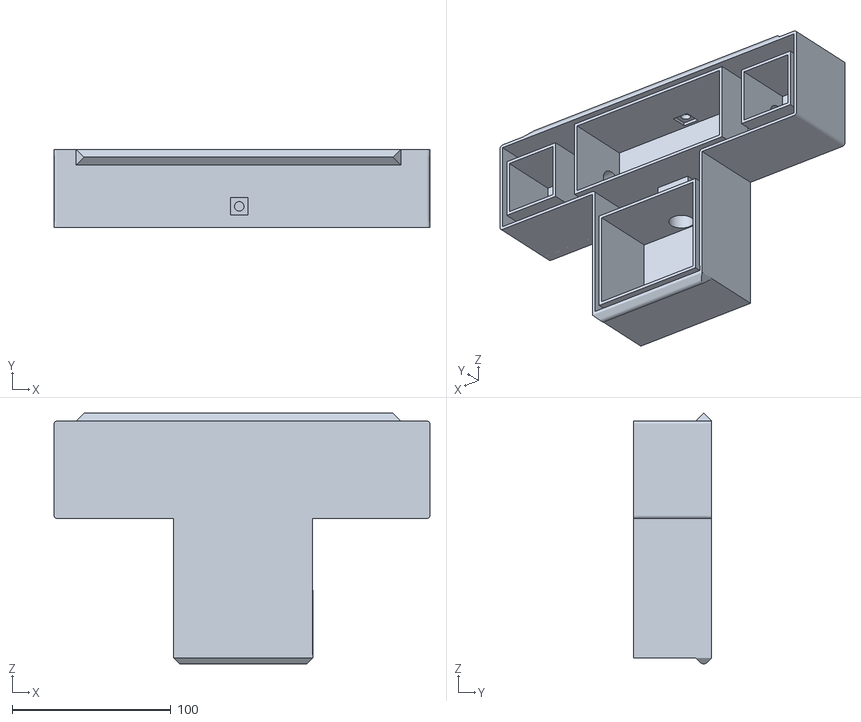
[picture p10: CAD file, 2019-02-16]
CAD/bottomHousing_woPole.stl
237.1 x 49.5 x 158.2

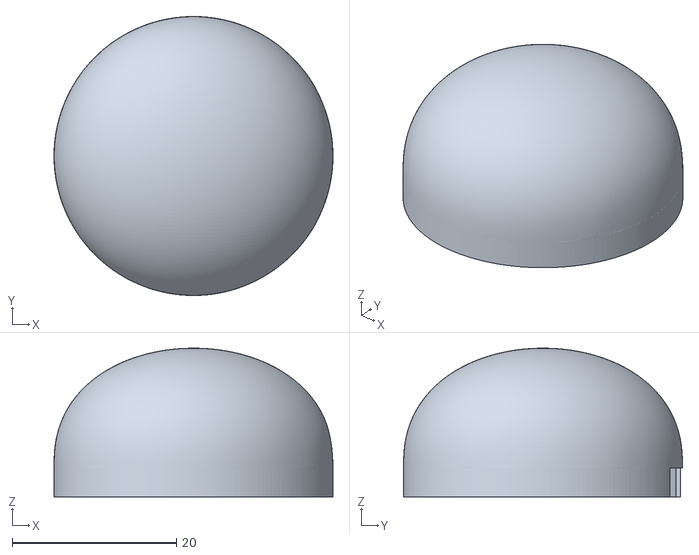
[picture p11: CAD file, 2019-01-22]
CAD/blackBody_dome.stl
34.0 x 34.0 x 18.1

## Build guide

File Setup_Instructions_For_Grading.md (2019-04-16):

# How to setup the pyranometer for grading purposes
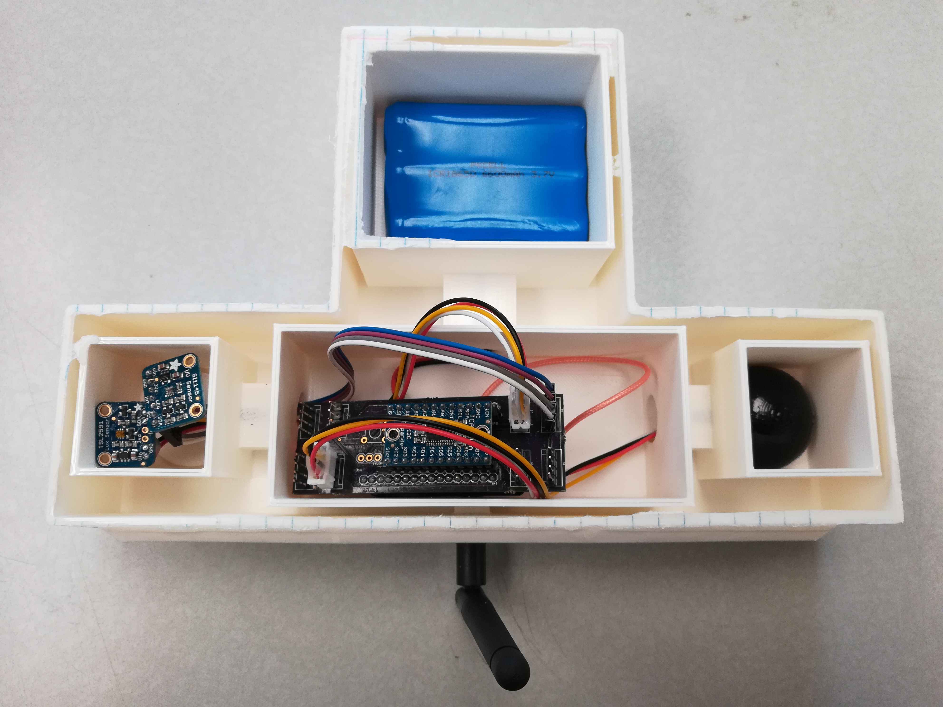
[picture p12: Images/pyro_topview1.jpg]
Complete setup


## What you will need
There are several pieces of hardware and software that are needed to setup the pyranometer correctly.

If you only need to compile and run the programs (not worry about all of the sensors, wireless communication, wireless power, and data upload), then you only need the following hardware:
- [Adafruit Feather M0 RFM95 LoRa Radio (900MHz)](https://www.adafruit.com/product/3178) -> You need two of these if you want hub and node running at the same time.

If you want to do a complete setup, you need all of the following:
- [Adafruit Feather M0 RFM95 LoRa Radio (900MHz)](https://www.adafruit.com/product/3178) -> Performs all computations, controls the sensors, and wirelessly sends the gathered data. Two of these are needed.
- [Adalogger FeatherWing](https://www.adafruit.com/product/2922) -> Logs gathered data to an SD card and interfaces with the multiplexer.
- [Adalogger Ethernet Featherwing](https://www.adafruit.com/product/3201) -> Gives Feather M0 Ethernet capabilities.
- OPEnS lab customer PCB board (provided by OPEnS lab) -> Allows multiple I2C sensors to be easily used with the Feather M0.
- [TCA9548A I2C Multiplexer](https://www.adafruit.com/product/2717) -> Allows the Feather M0 to use mutliple I2C sensors.
- [Adafruit TSL2591](https://www.adafruit.com/product/1980) -> Allows the capture of luminous flux of infrared and visible light.
- [TMP007 Thermopile](https://www.adafruit.com/product/2023) -> Reads the temperature of an object using its emitted infrared radiation.
- [SI1145 Light Sensor](https://www.adafruit.com/product/1777) -> Used to read UV index.

There are a few other parts that attach to the Feather M0, but are not chips:
- [2.4GHz Dipole Swivel Antenna](https://www.adafruit.com/product/944) -> Uses to transmit data over long distances.
- [Lithium Ion Polymer Battery - 3.7v 2500mAh](https://www.adafruit.com/product/328) -> Used in conjuntion with Powerboost to power the pyranometer.
- [1 1/4'' Acrylic Dome](https://kitkraft.com/products/1-1-4-31-8mm-clear-domes) -> Used to let IR light through.
- [2'' Acrylic Dome](https://kitkraft.com/products/2-50-4mm-clear-domes) -> Used in conjunciton with the smaller dome to let IR light through.
- [Glass Sheet](https://www.goodybeads.com/store/products/A013863.htm?gclid=EAIaIQobChMI_q3O9Liq4AIVjeNkCh3AEAxFEAQYASABEgL-IPD_BwE) -> Used to let UV and visible light through. 
- Ethernet connection to the hub device.

There is also a 3D printed housing structure, but it is not neccessary to use the pyranometer, so you should no have to worry about printing it out.

In terms of software, the only changes necessary for the code is to change the mac addresses for the ethernet. Each ethernet connection will require a different set of mac addresses. The current code works for an ethernet connection in OPEnS lab. The changes should be in config.h for only the hub code.

## Installing the Arduino IDE
In order to compile the programs and flash the Feather M0, the Arduiono IDE is needed. 
- Follow the instructions [here](https://learn.adafruit.com/adafruit-feather-m0-basic-proto/setup) to install the latest Arduino IDE for your specific OS. We have been using Windows, but any OS should work.
- Follow the instructions [here](https://learn.adafruit.com/adafruit-feather-m0-basic-proto/using-with-arduino-ide) to install the SAMD libraries for the Feather M0 board.

## Getting the code
- Run the following Git command to copy the repo to your local machine:
$git clone https://github.com/porterga/Senior-Project-Group3-Pyranometer.git
- The source code is in LOOM/
- The CAD files are in /CAD
- The Requirements document and Design Document are in Spring2019_docs/

## Setting up and running the hub
- Navigate to /LOOM/hub and open LOOM_library.ino with the Arduino IDE.
- Go to File at the top of the IDE and open up Preferences. Under "Sketchbook location", click browse. Select /LOOM/hub/LOOM_library. This lets Arduino know where to look for libraries.
- Change the mac addresses if the hub ethernet connection is not in OPEnS lab. The changes should be made in config.h of the hub code. Search for "is_ethernet" and change the values of the "byte mac[]" array.
- Plug in the Feather M0 and wait for your computer to detect/setup the device. Windows 10 does this automatically.
- Go to Tools at the top of the IDE and select "Adafruit Feather M0" as the board.
- Go to Tools at the top of the IDE and select the port the Feather M0 is connected to (typically COM 11). COM port will not appear if no Feather M0 is plugged in.
- To compile the code, click "Verify" (circle with a checkmark) in the top left corner of the IDE.
- To flash the Feather M0 with the hub code, click "Upload" (circle with right pointing arrow) in the top left corner of the IDE.
- The hub will now be operational.

## Setting up and running the node
- Navigate to /LOOM/node and open LOOM_library.ino with the Arduino IDE.
- Go to File at the top of the IDE and open up Preferences. Under "Sketchbook location", click browse. Select /LOOM/node/LOOM_library. This lets Arduino know where to look for libraries.
- Plug in the Feather M0 and wait for your computer to detect/setup the device. Windows 10 does this automatically.
- Go to Tools at the top of the IDE and select "Adafruit Feather M0" as the board.
- Go to Tools at the top of the IDE and select the port the Feather M0 is connected to (typicall COM 11). COM port will not appear if no Feather M0 is plugged in.
- To compile the code, click "Verify" (circle with a checkmark) in the top left corner of the IDE.
- To flash the Feather M0 with the node code, click "Upload" (circle with right pointing arrow) in the top left corner of the IDE.
- The node will now be operational.

Note that the node and hub will not do a whole lot on their own. In order to see the pyrometer working as intended, you will need to wire up the sensors, connect the antennas, connect the batteries, and connect the hub to the internet.

## Making the hub operational
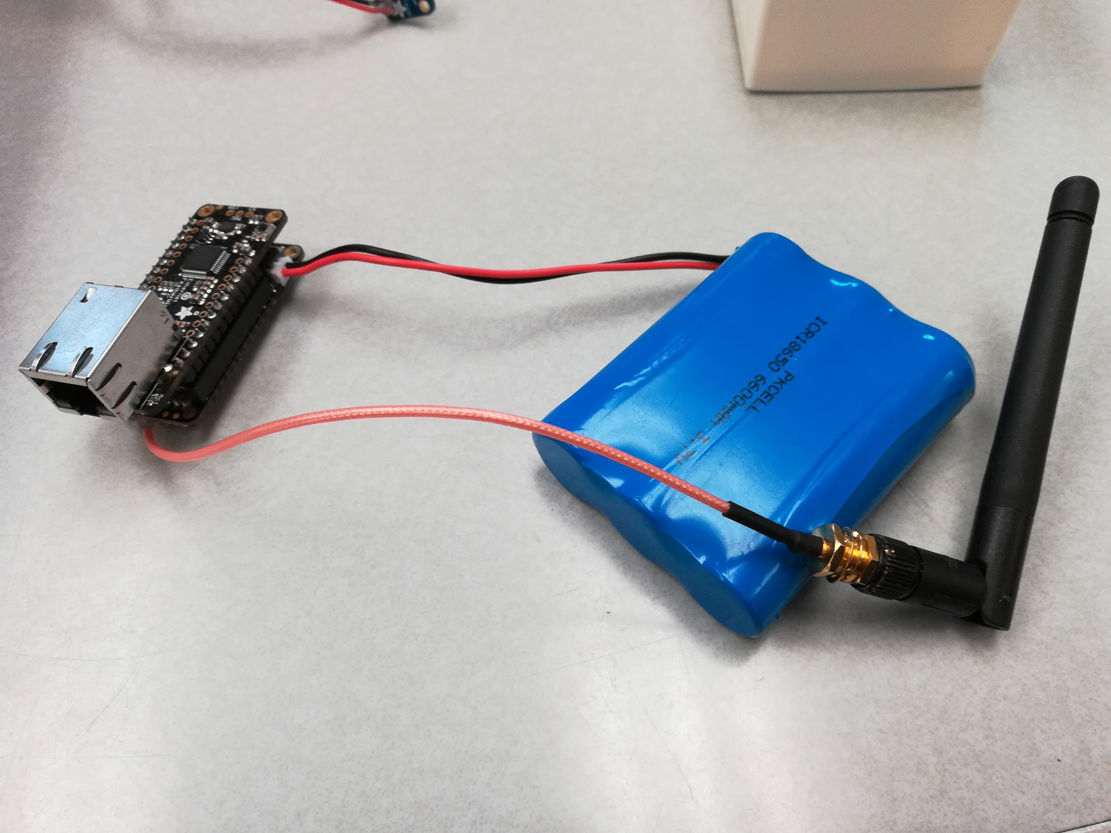
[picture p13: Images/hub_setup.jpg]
Hub setup

- Connect the antenna to the bottom of the Feather M0 that is flashed with the hub code. 
- Attach the Ethernet Featherwing to the Feather M0.
- Connect an ethernet cable to the Ethernet Featherwing.
- Connect a 3.7v Lipo battery to the Feather M0.

## Making the node operational
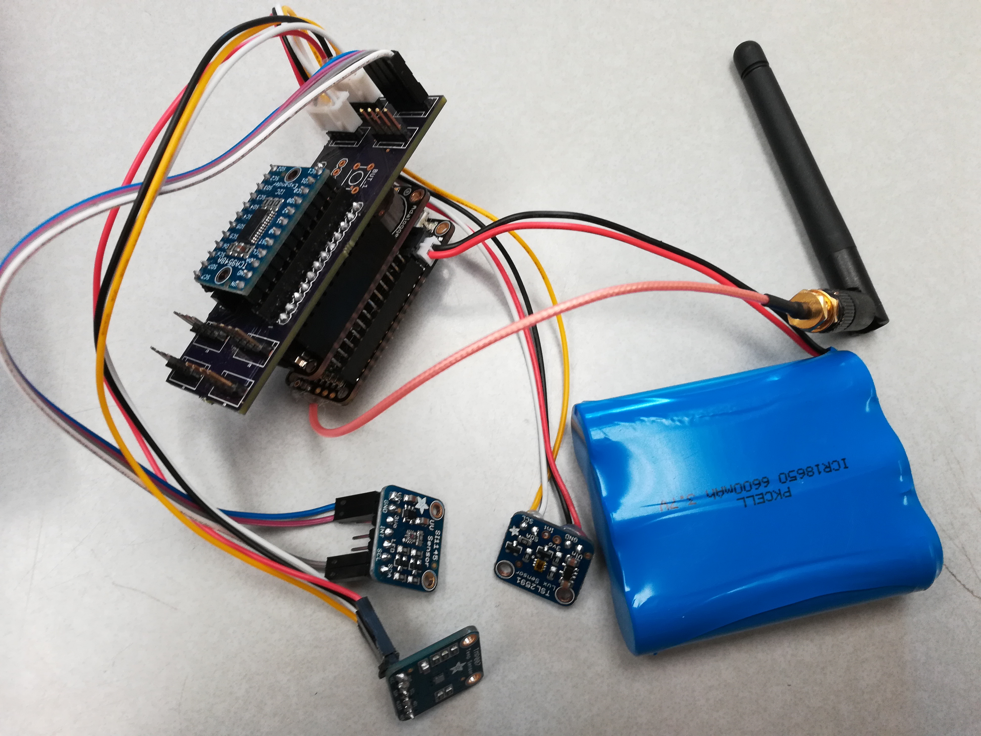
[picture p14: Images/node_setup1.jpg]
Hub setup

- Connect the Adalogger Featherwing to the Feather M0.
- Connect the OPEnS lab custom PCB to the Adalogger Featherwing.
- Connect the Adafruit multiplexer to the custom PCB.
- Connect the 3 I2C sensors (TMP007, SI1145, TSL2591) to the custom PCB.
- Connect the antenna to the bottom of the Feather M0
- Connect a 3.7v Lipo battery to the Feather M0.

## Watching the data live
- Go to https://docs.google.com/spreadsheets/d/19apKKsIjwD41yVsG-w3Wi7nnn5LLyrmbsgc1hVF8juA/edit?usp=sharing to see the pyranometer data being uploaded in real time. If everything was hooked up properly and the hub has internet access,data should be uploaded periodically. Data is uploaded to tab 3.

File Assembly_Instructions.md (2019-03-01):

# How to operate and assemble the OPEnS Lab Pyranometer

## Gathering materials
All materials for the OPEnS lab pyranometer can be found below. Substitutions can only be made where specified.

There are several chips that are needed, and they are as follows:
- [Adafruit Feather M0 RFM95 LoRa Radio (900MHz)](https://www.adafruit.com/product/3178) -> Performs all computations, controls the sensors, and wirelessly sends the gathered data.
- [Adalogger FeatherWing](https://www.adafruit.com/product/2922) -> Logs gathered data to an SD card and interfaces with the multiplexer.
- OPEnS lab customer PCB board (provided by OPEnS lab) -> Allows multiple I2C sensors to be easily used with the Feather M0.
- [TCA9548A I2C Multiplexer](https://www.adafruit.com/product/2717) -> Allows the Feather M0 to use mutliple I2C sensors.
- [Adafruit TSL2591](https://www.adafruit.com/product/1980) -> Allows the capture of luminous flux of infrared and visible light.
- [TMP007 Thermopile](https://www.adafruit.com/product/2023) -> Reads the temperature of an object using its emitted infrared radiation.
- [SI1145 Light Sensor](https://www.adafruit.com/product/1777) -> Used to read UV index.
- [PowerBoost 500 Charger](https://www.adafruit.com/product/1944) -> Used to boost 3.7v to 5.2v.
- **Note that all of these chips need to be soldered**
- **Total Cost = $97.65**

There are a few other parts that attach to the Feather M0, but are not chips:
- [2.4GHz Dipole Swivel Antenna](https://www.adafruit.com/product/944) -> Uses to transmit data over long distances.
- [Lithium Ion Polymer Battery - 3.7v 2500mAh](https://www.adafruit.com/product/328) -> Used in conjuntion with Powerboost to power the pyranometer.
- [1 1/4'' Acrylic Dome](https://kitkraft.com/products/1-1-4-31-8mm-clear-domes) -> Used to let IR light through.
- [2'' Acrylic Dome](https://kitkraft.com/products/2-50-4mm-clear-domes) -> Used in conjunciton with the smaller dome to let IR light through.
- [Glass Sheet](https://www.goodybeads.com/store/products/A013863.htm?gclid=EAIaIQobChMI_q3O9Liq4AIVjeNkCh3AEAxFEAQYASABEgL-IPD_BwE) -> Used to let UV and visible light through. 
- **Total Cost = $40.25**

The last required materials are plastic for 3D printing. Depending on your 3D printer, you may need different diameter plastic:
- [Black PLA](https://www.amazon.com/SainSmart-PLA-157-PLA-Filament-Black/dp/B00AA5AJUG) -> Used to print the black-body dome.
- [White ABS](https://www.amazon.com/Octave-White-ABS-Filament-Printers/dp/B007X0QBOO) -> Used to print the housing structure.
- **Total cost = $42**

**Total cost of materials is approximately $178**

## Printing the Structure and Black-Body Dome
The entire structure, save for the glass and acrylic, is 3D printed. The project consists of 3 different prints: the lid, the main container, and the black-body dome. The total time of printing everything is about 18 hours. It is recommended to first print the lid, then print the main container over night, and print the black-body dome last. Instructions on how to print the objects will vary depending on the printer and slicing software being used, but below are general instructions:

**Printing the Lid**

- Download the lid CAD design found in this repo at /CAD/lid.stl.
- Load lid.stl into your slicing software.
- Orient the lid such that the top of the lid is touching the bed of the 3D printer. The sides of the lid should be on top.
- Select ABS as the material being used.
- Select standard level of detail with 30% infill.
- Add brim to go around the base of the object.
- DO NOT ADD SUPPORT -> Support may cause problems with latching the lid to the main container.
- Slice the object and generate a .gcode file.
- Load the white ABS filament into your 3D printer.
- Load your .gcode file into the 3D printer.
- Spray an even layer of hairspray on the bed.
- Start the print.
- Watch the first couple layers and make sure the plastic layers are not peeling off the bed.
- Once the print job is complete, use a paint scraper to carefully pry the lid from the bed.
- **Total Print Time = 5-7 hours**

**Printing the Main Container**

- Download the lid CAD design found in this repo at /CAD/main_container.stl.
- Load main_container.stl into your slicing software.
- Orient the main container such that is is upright, as in the floor of the container is against the 3D printer bed.
- Select ABS as the material being used.
- Select standard level of detail with 30% infill.
- Add brim to go around the base of the object.
- DO NOT ADD SUPPORT -> Support may cause problems with latching the lid to the main container.
- Slice the object and generate a .gcode file.
- Load the white ABS filament into your 3D printer.
- Load your .gcode file into the 3D printer.
- Spray an even layer of hairspray on the bed.
- Start the print.
- Watch the first couple layers and make sure the plastic layers are not peeling off the bed.
- Once the print job is complete, use a paint scraper to carefully pry the lid from the bed.
- **Total Print Time = 9-12 hours**

**Printing the Black-Body Dome**

- Download the lid CAD design found in this repo at /CAD/dome.stl.
- Load dome.stl into your slicing software.
- Orient the dome such that is is upright, as in the object looks like an upside-down bowl.
- Select PLA as the material being used.
- Select standard level of detail with 30% infill.
- Add brim to go around the base of the object.
- DO NOT ADD SUPPORT -> Removing the support is exceedingly difficult and is not needed.
- Slice the object and generate a .gcode file.
- Load the black PLA filament into your 3D printer.
- Load your .gcode file into the 3D printer.
- Spray an even layer of hairspray on the bed.
- Start the print.
- Watch the first couple layers and make sure the plastic layers are not peeling off the bed.
- Once the print job is complete, use a paint scraper to carefully pry the lid from the bed.
- Once done, use a scale to measure the mass of the dome in kilograms and take note of it. The mass will be used later when calculating total W/m^2.
- **Total Print Time = 20-30 minutes**

Make sure the objects are sturdy and are not warped. The lid should latch onto the top of the main container with only a small amount of effort. Be careful not to crack the outer wall of the main container; be gentle!

## Flashing the Feather M0
The Feather M0 needs to have the LOOM software loaded onto it in order for it to function. The following instructions will help ensure the Feather M0 is ready to begin controlling the pyranometer:

- Follow the instructions [here](https://learn.adafruit.com/adafruit-feather-m0-basic-proto/setup) to install the Arduino IDE.
- Follow the instructions [here](https://learn.adafruit.com/adafruit-feather-m0-basic-proto/using-with-arduino-ide) to install the proper libraries.
- Download the folder /LOOM/node and save it to a convenient location.
- Navigate to the folder and open /node/LOOM_library.ino.
- In the top left folder click "File"->"Preferences".
- Change the sketch location to be the file path to LOOM_library.
- Navigate to the file /LOOM_library/loom_tmp007.h
- search for the term "double mass".
- On the right hand side of the equal side, change the value to the exact mass of the black-body dome in kilograms.
- Save the file.
- Connect the Feather M0 to your computer using a USB/USB-C cable. 
- In the top left corner click the "upload button" (it looks like an arrow pointing right).
- If the terminal at the bottom reports no errors and says "CPU reset successfully" as the last message, the Feather M0 was successfully flashed.
- Disconnect the Feather M0, note that the LOOM software remains in the Feather M0 and will restart each time the Feather M0 is powered on.

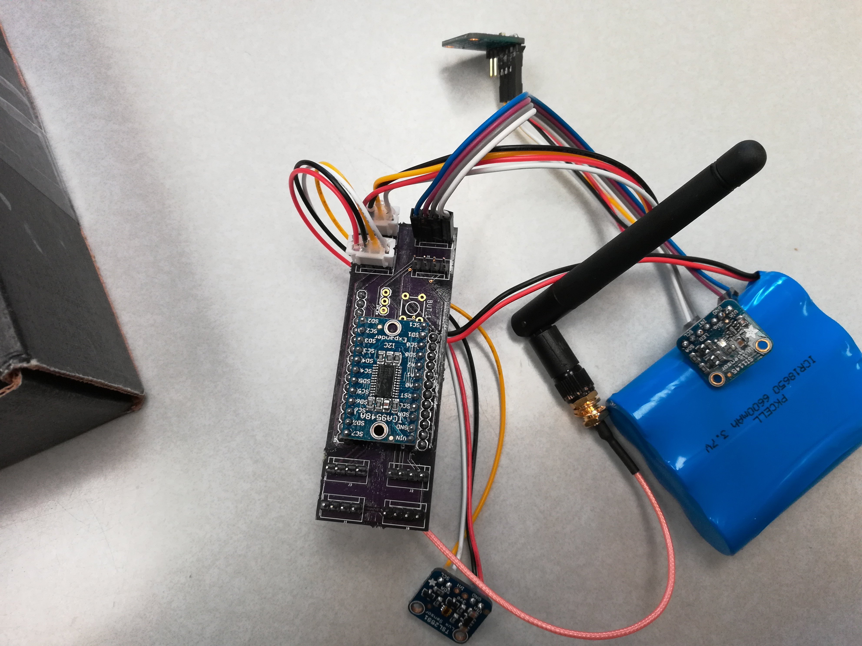
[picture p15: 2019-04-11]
Images/node_setup2.jpg

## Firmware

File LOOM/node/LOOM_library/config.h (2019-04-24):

// ================================================================ 
// ===                   CONFIGURATION FILE                     === 
// ================================================================
//
// Use this file to configure the device you are flashing the firmware of
//
// This file is divided into two sections:
//
//  Options: The top half that can be modified to change common settings
//
//  Advanced Options: the bottom section that is at least partially set based on  
//    the top half but may be modified for more specific behavior. 
//    Also contains other specific options that don't need to change as frequently
//
// Definitions that should not be modified by the user are
//   located in the library and are not present here

// ================================================================
// ================================================================ 
// ===                     PRIMARY OPTIONS                      === 
// ================================================================
// ================================================================



// ================================================================ 
// ===                  IDENTIFICATION OPTIONS                  === 
// ================================================================
// --- Device Identification --- 
#define FAMILY 		"LOOM"		// Will usually be "LOOM", you can change this if you are setting up your own network
#define FAMILY_NUM       5		// Specifies the subnet of the family that the device is on. 0 for elevated permissions (can communicate with any subnet), 1-9 for normal
#define CHANNEL          1		// Channel to use. Set to 1-8 for channels A-H, respectively (on WiFi), LoRa can use 1-9. Alternatively can define to -1 to used advanced option INIT_INST
#define REQUEST_SETTINGS 0		// 1 to request dynamic channel settings (i.e. next available channel) from MaxMSP Channel Manager, 0 to not
#define AUTO_NAME        1		// 1 to enable naming device based on configured settings (if not set manual name in advanced options)
#define CUSTOM_NAME "Custom"	// This is only used if Auto_name is set to be 0


// ================================================================ 
// ===                      SERIAL OPTIONS                      === 
// ================================================================
// --- Debugging --- 
#define LOOM_DEBUG    0			// Set to 1 if you want Serial statements from various functions to print
								// NOTE: Serial monitor must be opened for device to setup if this is enabled
								//   Device will freeze if this in enabled and device does not get plugged into Serial
								// LOOM_DEBUG_Print* are Serial prints that are removed if debugging is off

#define dynamic_serial_output 0 // These only apply if LOOM_DEBUG is enabled
								// 0 is standard operation 
								//   - Serial monitor needs to start / be open for device to setup
								//   - Serial (USB) can generally be detached after setup without issue 
								//   - Note that you may need to reopen the Serial monitor if it was open before the device was plugged back in
								// 1 Allows serial monitor to device to setup when LOOM_DEBUG is enabled without Serial (USB) being attached 
								//   - Note that you probably want to have the serial monitor open before uploading to the device, else you may miss 
								//     the first Serial prints, as enabling this option means that the device does not wait for you to open Serial

#define wake_delay 0			// 1 to enable wait 5 seconds upon awaking from sleep to (re)start Serial before program continue (useful for reprogramming if device quickly goes back to sleep)


#define prevent_platform_compile_error 1  	// 0: Allow errors to be triggered if the program calls 
											//     functionality of platforms / devices that are not enabled
											// 1: Permits the code to compile and the device will skip functionality
											//     of platforms / devices that are not enabled, informing the user of such

#define display_config 0		// 1 to print the uploaded configuration at start of setup, 0 to not

// ================================================================ 
// ===                  DEVICE TELEMETRY TYPE                   === 
// ================================================================
#define hub_node_type 1		// 0: Hub, 1: Node
#define is_repeater   0		// Sorry, this doesn't do anything yet


// ================================================================ 
// ===              PREDEFINED AGGREGATE DEVICES                === 
// ================================================================
// Enable specified devices, typically mutually exclusive
// Further options in the advanced settings
// Can override settings defined before the aggregate devices

#define is_ishield      0	// 1 to specify using Ishield (generally used on WiFi)
#define is_multiplexer  1	// 1 to specify Multiplexer (tca9548a) is being used
#define is_sapflow      0	// 1 to specify Sapflow  
#define is_evaporimeter 0	// 1 to specify Evaporimeter


// ================================================================ 
// ===                 COMMUNICATION PLATFORMS                  === 
// ================================================================
#define is_wifi       0		// 1 to enable WiFi
#define is_lora       1		// 1 to enable LoRa (cannot be used with nRF) (Further customization in advanced options)
#define is_nrf        0		// 1 to enable nRF (cannot be used with LoRa) (Further customization in advanced options)
#define is_ethernet   0		// 1 to enable Ethernet (a number of options below might auto enable this anyway though)
#define is_fona       0		// 1 to enable cellular via Fona (808 version)


// ================================================================ 
// ===                  DATA LOGGING PLATFORMS                  === 
// ================================================================
#define is_pushingbox 0		// 1 to enable PushingBox  
// #define is_adafruitio 0		// 1 to enable Adafruit IO (currently requires WiFi) [not much support yet]

// --- RTC Options ---
#define is_rtc        0		// Enable RTC functionality
#if is_rtc == 1
	#define RTC_pin 6		// What pin the RTC interrupt is connected to

	// Select only one of the below options
	#define is_rtc3231 0 	// RTC DS 3231 Featherwing
	#define is_rtc8523 1	// RTC Adalogger Featherwing with PCF8523 RTC (the one with SD card)
#endif

// --- SD Options ---
#define is_sd         1		// 1 to enable SD card 
#if is_sd == 1
	// Does NOT automatically save to SD
	// This works more like a filter than an automator,
	// with a minimum of sdSaveMinDelay between saves
	// Uses millis
	#define sdSaveFilter  	 1 	// 1 to enable a millis delay to SD 
	#define sdSaveMinDelay   1  // minimum delay in seconds between saves (only applies sdSaveFilter is 1)

	#define sdBroadcastSave  0  // 1 to broadcast on communication platforms when data is saved to SD, 0 to not 
#endif


// ================================================================ 
// ===                        ACTUATORS                         === 
// ================================================================

// --- Enabled Actuators --- 
#define num_servos    0 	// Number of servos being used (up to 8 per shield, testing has generally only been through 1 shield)
#define num_steppers  0		// Number of stepper motors being used 
#define is_relay      0		// 1 if a relay is being used
#if is_relay == 1
	#define relay_pin 10	// Digital pin connected to the relay enable 
#endif



// ================================================================ 
// ===                         SENSORS                          === 
// ================================================================

// --- Button Options ---
#define is_button 		1	// 1 to enable button
#define button_pin 		10	// Pin button is attached to 

// --- Analog Setting --- 
#define is_analog     0		// 1 if analog input is being used, 0 if not

	#define is_analog_a0 1 
	#define is_analog_a1 1
	#define is_analog_a2 0
	#define is_analog_a3 0
	#define is_analog_a4 0
	#define is_analog_a5 0

#define analog_samples 16 	// Must be 1, 2, 4, 8, or 16 number of analog measurements to sample and average



// --- Decagon Soil Moisture ---
#define is_decagon    0		// 1 if GS3 Decagon is being used

// --- I2C Sensors ---
// Using I2C sensors without the multiplexer
// Multiplexer / aggregate device may override these settings
#define is_tsl2591         1	// Lux Sensor
#define is_tsl2561         0	// Lux Sensor
	#if is_tsl2561 == 1
		#define tsl2561_res 3 // 1 for fastest, low-res, 2 for middle, 3 for slow, high-res
		// #define is_tsl2561_low   1 
		// #define is_tsl2561_float 1
		// #define is_tsl2561_high  1
	#endif
#define is_veml6075		     0	// UV sensor
#define is_si1145		       1	// New UV sensor
#define is_tmp007		       1	// thermopile
#define is_fxos8700        0	// Accelerometer / Magnetometer
#define is_fxas21002       0	// Gyroscope
#define is_zxgesturesensor 0	// ZX_Distance Sensor
#define is_sht31d          0	// Temperature / Humidity
#define is_mb1232          0	// Sonar
#define is_mpu6050         0	// Accelerometer / Gyroscope
#define is_lis3dh          0	// Accelerometer
#define is_ms5803          0	// Atmospheric Pressure / Temperature Sensor
#define is_ads1115         1  // ADC converter
#define is_hx711           0    // Load Cell
	#if is_hx711 == 1
		#define hx711_calibration 961.275
	#endif


// ================================================================ 
// ===                     WIFI SETTINGS                        === 
// ================================================================
// --- WiFi Settings ---
// Requires is_wifi to be set to 1 to take effect
#if is_wifi == 1
	#define DEFAULT_MODE      WPA_CLIENT_MODE	// AP_MODE, WPA_CLIENT_MODE or WEP_CLIENT_MODE
	#define DEFAULT_NETWORK   "OPEnS"			// Network SSID / name
	#define DEFAULT_PASSWORD  "arduino101"		// Network password
#endif




// ================================================================
// ================================================================ 
// ===                    ADVANCED OPTIONS                      === 
// ================================================================
// ================================================================

// --- Flash Options ---
#define enable_flash 0   			// 1 is the default, 0 to turn of reading and writing to flash/EEPROM memory 

// --- Scripts ---
#define enable_hub_scripts 0		// RPN script parser

// --- Advanced Interdev Communication ---
#define advanced_interdev_comm   0	// 1 to use Max-like functionality
#define build_actuator_cmd_funcs 0  // 1 to include file to make commands for Loom actuators

// --- MPU6050 Options
#define skip_mpu_cal 1


// --- Set Custom Instance Number and UDP Port ---
// If not using channels, then the following 
// intial instance number and port (if WiFi) will be used
// Interdevice communication is undefined and less supported
// when not using channels
#if CHANNEL == -1
	#define INIT_INST   	 3	// Initial device instance number (normally 1-9 when using channels)
	#if is_wifi == 1
		#define INIT_PORT 9443	// Initial device UDP port (normally 1-9 when using channels)
	#endif
#endif

#if is_wifi == 1
	#define advanced_interdev_comm 1 	// Enable for full Max support 
										// Default is for this to be 1 when using WiFi
#endif

#if LOOM_DEBUG == 1
	#define SERIAL_BAUD 115200 			// Select Serial baudrate, only used supported rates (i.e. 9600, or 115200, etc.)
										// Make sure the Serial monitor is set to the same baud
#endif
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

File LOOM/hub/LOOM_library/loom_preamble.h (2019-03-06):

// ================================================================ 
// ===                    FILE DESCRIPTION                      === 
// ================================================================

// This file uses the config.h file to define various other constants
//  and to select with files to include.
// This file also includes a various macros and function prototypes
//  that are used throughout the code

// ================================================================ 
// ===                        LIBRARIES                         === 
// ================================================================
#include <OSCBundle.h> // All LOOM devices rely on the Arduino OSC library in some way


// ================================================================ 
// ===               DEFINITIONS BASED ON CONFIG                === 
// ================================================================


#define VBATPIN A7                // Pin to check for battery voltage


// --- WiFi UDP Ports ---
#if is_wifi == 1
	#define GLOBAL_PORT 	9400
	#define SUBNET_PORT     GLOBAL_PORT+(10*FAMILY_NUM)	
#endif

// --- Instance and port if using channels ---
#if CHANNEL >= 1 && CHANNEL <= 9
	#define INIT_INST CHANNEL
	#if is_wifi == 1
		#define INIT_PORT SUBNET_PORT+CHANNEL
	#endif
#endif

// ================================================================
// ===              AUTOMATICALLY SET DEVICE NAME               ===
// ================================================================

#if AUTO_NAME == 1
	// Make sure only one device type is enabled
	#if ( (is_ishield) + (is_evaporimeter) + (is_sapflow) + (num_servos > 0) + (num_steppers > 0) + (is_relay) + (is_decagon) + (is_multiplexer) ) > 1
		autoname_device_type_error_probably_incompatible_devices_defined_in_config // this will force an error if too many sensor/actuator were defined (needs to be = 1 for autoname to work)
	#endif

	// Automatically set device name
	#if   is_ishield 
		#define DEVICE "Ishield"
	#elif num_servos > 0
		#define DEVICE "Servo"
	#elif num_steppers > 0
		#define DEVICE "Stepper"
	#elif is_relay
		#define DEVICE "Relay"
	#elif is_decagon
		#define DEVICE "Decagon"
	#elif is_multiplexer
		#define DEVICE "Mux"
	#elif is_sapflow
		#define DEVICE "Sapflow"
	#elif is_evaporimeter
		#define DEVICE "Evap"
	#else
		#define DEVICE "Unknown"
	#endif
#else
	// --- Custom Device Identification --- 
	#define DEVICE CUSTOM_NAME // The device name (can be changed), used only if not using automatic device name
#endif
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

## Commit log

2018-12-13 created a crude dome to cover thermopile
    [dome_prototype.f3d]
2018-12-13 created some domes, one design should have correct dimensions for thermopile
    [3_domes.f3d, cleaner_dome.f3d, thermopile_dome_final.f3d]
2018-12-14 added thickness to dome and a cavity for wires
    [thermopile_dome_final.f3d]
2018-12-15 added thermopile section of structure
    [Thermopile_section.f3d, thermopile_dome_final.f3d]
2019-01-09 These are two thermopile sections to prototype
    [2_thermopile_sections.f3d]
2019-01-12 Dome print file
    [dome_to_print.stl]
2019-01-12 cleaning up CAD files
    [3_domes.f3d, cleaner_dome.f3d, dome_prototype.f3d, thermopile_dome_final.f3d]
2019-01-12 Added Fusion 360 dome
    [Final_dome.f3d]
2019-01-13 Entire bottom of housing structure
    [Bottom_housing_structure.stl]
2019-01-13 Bottom of housing, can open in Fusion360
    [Fusion_360_housing_bottom.f3d]
2019-01-13 container for pyranometer, lid coming soon
    [pyro_container.stl]
2019-01-13 file containing lid, box, and pyro - Fusion360
    [Fusion_360_lid+box+pyro.f3d]
2019-01-13 Cleaned up CAD folder
    [2_thermopile_sections.f3d, Thermopile_section.f3d]
2019-01-14 Rotated object
    [dome_to_print.stl]
2019-01-15 Added antenna hole
    [Bottom_housing_structure.stl]
2019-01-15 lid that goes over top of container
    [lid.stl]
2019-01-15 added gcode files and updated main file
    [Fusion_360_lid+box+pyro.f3d]
2019-01-15 trimmed box and lid
    [lid.stl, pyro_container.stl]
2019-01-22 Made the dome larger and thinner
    [dome_to_print.stl]
2019-01-22 Repaired and rotated dome
    [dome_to_print.stl]
2019-01-22 Increased size and removed LoRa chip box
    [Bottom_housing_structure.stl]
2019-01-28 Lid and walled bottom structure
    [Lid.stl, bottom_housing.stl]
2019-02-13 Cleaning up CAD folder
    [Final_dome.f3d, Fusion_360_housing_bottom.f3d, Fusion_360_lid+box+pyro.f3d, Lid.stl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]
2019-02-16 rounded edges and shorted one latch to make lid easier to put on
    [bottomHousing_withPole.stl, bottomHousing_woPole.stl, lid.stl]
2019-02-27 updated libraries and lux sensor is now logged alongside tmp007
2019-03-01 Added printing instructions
2019-03-11 fully integrated SI1145 sensor. Improved data reported; removed analog sensor enable
2019-03-11 changed lux sensor to report IR and Vis individually and together
2019-03-14 changed mass of dome, modified data name for UV sensor
2019-03-14 modified bundled data for lux sensor, turned flash on
2019-03-15 Removed LOOM_DEBUG and display_config; everything now runs off battery
2019-04-15 Added Spring term docs
